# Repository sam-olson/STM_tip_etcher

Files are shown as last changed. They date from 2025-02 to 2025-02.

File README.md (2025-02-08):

# STM Tip Etcher

## Preliminary
This repository contains design files for building a microcontroller-based etcher for creating scanning tunneling microscopy (STM) tips from tungsten wire. The system works by applying a voltage between two tungsten electrodes immersed in an etchant (in this case, 1 M NaOH). The resistance between the two electrodes is monitored through a voltage divider formed between the electrodes and a 100 Ω reference resistor. The output voltage of the divider is read by an analog input pin on the microcontroller. When a spike in resistance between the etching electrodes is detected, a transistor switch shuts off power to the tip, preventing over-etching and rounding of the tip. Using tips etched via this system, high resolution STM images of highly-oriented pyrolytic graphite (HOPG) have been obtained.

The following items are required to assemble this system:

*Equipment*

- Soldering iron
- 3D-printer

*Parts (see the included Bill of Materials for sourcing)*

- Arduino Nano (x1)
- 300 Ω resistor (x1)
- 100 Ω resistor (x2)
- Green LED (x1)
- 2N3904 NPN transistor (x1)
- M4x6.4mm heat set insert (x2)
- M4x8mm set screw (x2)
- 5x7 cm perfboard (x1)
- M3x14mm socket head screw (x4)
- M3x11mm spacer (x4)
- M3x3.8mm heat set insert (x4)

## Build Instructions
### Assembling the Circuit

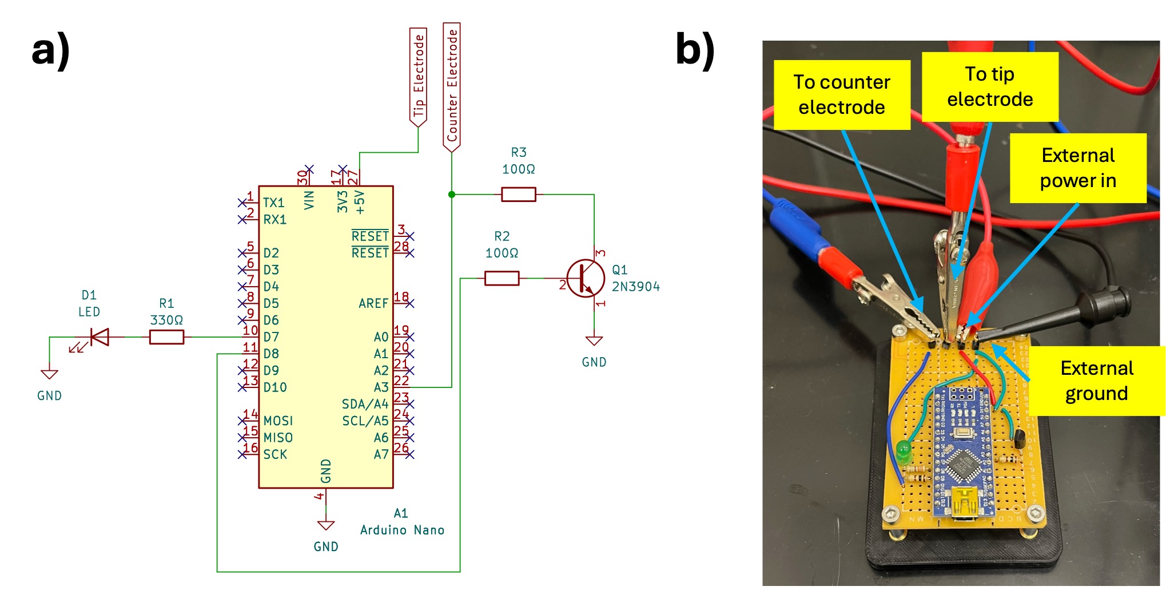
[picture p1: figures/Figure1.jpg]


Figure 1: a) Electrical schematic for the tip etching set up, b) assembled circuit board with header pins labeled

1. Solder electrical components onto a 5x7 cm perfboard following the schematic shown in Fig. 1
2. Power can be supplied to the electrodes from the Arduino’s 5V pin, or an external benchtop power supply
can be used if the current required is ≥ 500 mA or a different voltage is required. If an external power supply is used, it can also power the Arduino through the VIN pin (as long as the voltage is ≤ 12 V)
3. Header pins and alligator clip cables can be used for interfacing with the tungsten tip and counter electrodes

### 3D-Printing Components
3D-print the STEP files for the electrode holding fixture and the circuit board base in PLA (see Fig. 2).

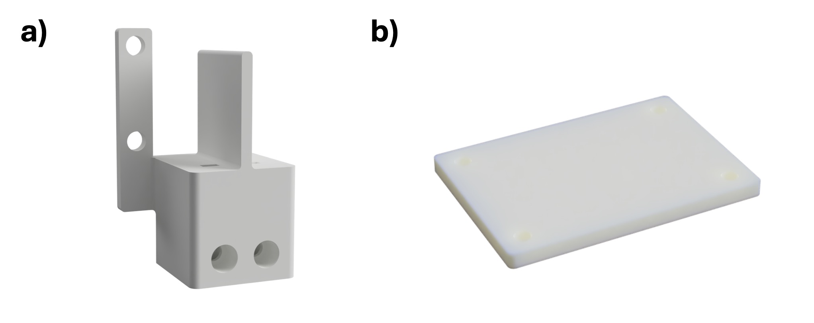
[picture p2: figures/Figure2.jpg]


Figure 2: Renders of 3D-printed components: a) electrode holding fixture (ElectrodeHoldingFixture.step), b) circuit board base (CircuitBoardBase.step)

### Preparing the Electrode Holding Fixture for Use

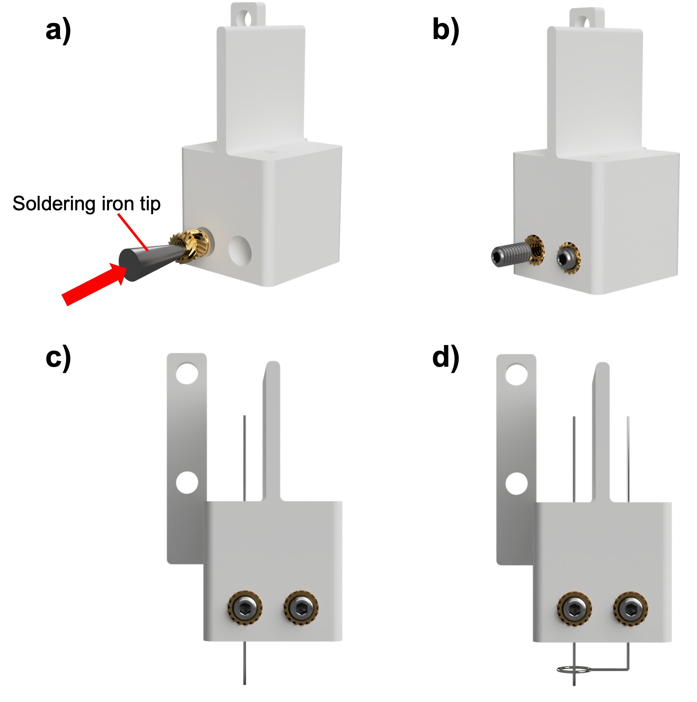
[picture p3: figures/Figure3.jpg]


Figure 3: a) Installing the M4x6.4mm threaded inserts into the electrode holding fixture using a soldering iron tip, b) installation of set screws, c) tip electrode added to electrode holding fixture, d) counter electrode added to electrode holding fixture

1. Using a soldering iron set to 250 °C, heat set two M4x6.4mm threaded inserts into the 6.2 mm holes on the front of the fixture (Fig. 3a)
2. Insert a M4x8mm set screw into each threaded insert, these will be used to press against the tungsten wires to hold them in place during etching (Fig. 3b)
3. Cut a 100 mm length of 0.25 mm diameter tungsten wire and form a 6 mm diameter loop at one end, this will serve as the counter electrode
4. Cut a 75 mm straight length of 0.25 mm diameter tungsten wire, this will serve as the tip electrode
5. Push the tip electrode through the rectangular hole on the left side of the bottom of the electrode holding fixture, leaving roughly 10 mm exposed at the bottom, and fasten it in place by tightening the set screw (Fig. 3c)
6. Push the straight end of the counter electrode through the rectangular hole on the right side of the bottom of the electrode holding fixture
7. Place a straight piece of 0.25 mm tungsten wire into the hole on the lefthand side of the top of the fixture and push it through until 14 mm of wire is exposed between the bottom of the fixture and the top of the loop
8. Create a 90° bend 7 mm from the top of the loop in the counter electrode and situate the loop so that the tip electrode sits in the middle (Fig. 3d)
9. The electrode holding fixture includes two M4-size holes for optional attachment to a stand, however the fixture can also easily be held in place via a lab stand clamp

### Attaching the Circuit Board to the Circuit Board Base

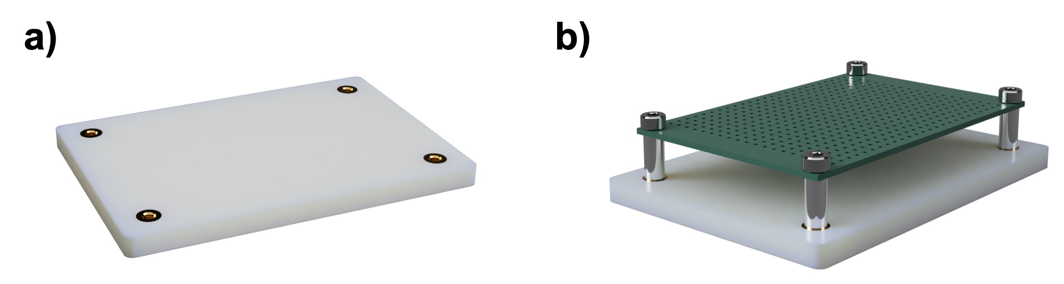
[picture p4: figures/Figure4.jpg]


Figure 4: a) Circuit board base with heat set inserts installed, b) circuit board base with circuit board and standoffs attached

1. Install four M3x3.8mm heat set inserts using a soldering iron set to 250 °C into the 5.5 mm diameter circular recesses on the top of the circuit board stand (Fig. 4a)
2. Place the M3x10mm unthreaded standoffs on the threaded inserts
3. Place the circuit board on top of the unthreaded standoffs and secure it in place with four M3x14mm socket screws (Fig. 4b)
4. Load the firmware (`STM_tip_etcher.ino`) onto the Arduino Nano via the Arduino IDE

## Using the Tip Etcher

### Running an Etch Recipe

1. Prepare an etchant solution of 1 M NaOH in a small dish
2. Attach the electrode holding fixture to a stand with two M4 screws, or place it into a lab stand clamp and lower it until both the tip electrode and the loop of the counter electrode are submerged just below the surface of the etchant
3. Using alligator clips, connect the tip electrode to the 5V pin of the Arduino (or an external power supply), and connect the counter electrode to the counter electrode header (the junction with the 100 Ω resistor and pin A3 on the Arduino)
4. If using an external power supply, ensure that the voltage is kept below 12V and that the ground is tied to the ground pin of the Arduino
5. Turn on the power supply/Arduino, this will begin the tip etching process
6. For a voltage of 5V, a counter electrode loop of 6 mm, and a 1 M NaOH etchant, the etch time is typically around 20 minutes
7. Once the bottom of the tip electrode drops off into the etchant, the resistance between the tip and counter electrode will increase drastically and the microcontroller will automatically stop the power to the electrodes to prevent overetching. The LED will illuminate at this point to indicate that the etching is complete

### Modifying the Firmware
The firmware for the system (`STM_tip_etcher.ino`) is designed to be easy to modify if necessary. There are two important variables for etch profile modification: the voltage threshold below which the etching halts (variable `v_threshold`), and the minimum etching time before cut off can occur (variable `t_threshold`). Variation in one of several experimental parameters can result in the need to modify the voltage and time thresholds. For example, a larger counter electrode diameter may result in a higher final resistance (and so a lower voltage threshold), while an increase in etchant molarity can result in a lower final resistance (and so higher voltage threshold) and/or a shorter etch time. The firmware prints the voltage reading to the serial port during etching, so it is advised to monitor this during several etches once the physical arrangement of your set up is finalized to determine where to set your thresholds.

## Results
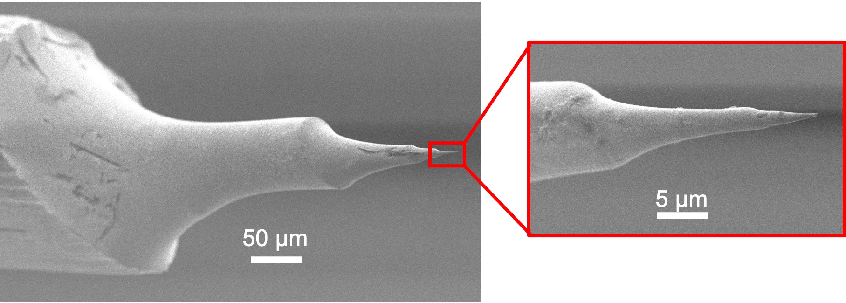
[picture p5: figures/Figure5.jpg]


Figure 5: An STM tip etched from 0.25 mm tungsten wire using this system

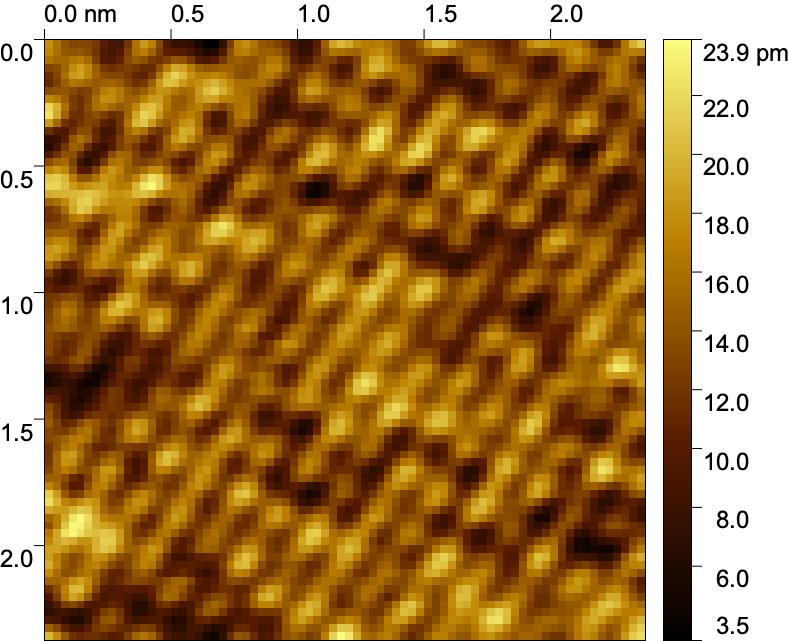
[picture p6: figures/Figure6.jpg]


Figure 6: STM micrograph of highly oriented pyrolytic graphite (HOPG) taken using a tip etched with this system

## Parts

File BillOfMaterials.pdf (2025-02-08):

ITEM | SUPPLIER | PART NUMBER | QUANTITY | | UNIT COST | EXTENDED
COST
ARDUINO NANO | Arduino | A000005 | 1 | $ 24.90 $ | 24.90
330 Ω RESISTOR | Digi-Key | CF14JT330RCT-ND | 1 | $ | 0.10 $ | 0.10
100 Ω RESISTOR | Digi-Key | CF14JT100RCT-ND | 2 | $ | 0.10 $ | 0.20
GREEN LED | Digi-Key | 754-1273-ND | 1 | $ | 0.27 $ | 0.27
2N3904 NPN TRANSISTOR | Digi-Key | 2N3904FS-ND | 1 | $ | 0.28 $ | 0.28
PERFBOARD 76.2X50.8 MM | Digi-Key | 3132-ST-PERF-2-3-ND | 1 | $ | 3.49 $ | 3.49
M3X14MM SOCKET HEAD SCREWS | McMaster-Carr | 91292A027 | 4 | $ | 0.08 $ | 0.31
M3X10MM SPACERS | McMaster-Carr | 94669A105 | 4 | $ | 0.56 $ | 2.24
M3X3.8MM HEAT SET INSERTS | McMaster-Carr | 94180A331 | 4 | $ | 0.20 $ | 0.80
M4X6.4MM HEAT SET INSERTS | McMaster-Carr | 94459A160 | 2 | $ | 0.22 $ | 0.44
M4X8MM SET SCREWS | McMaster-Carr | 92605A113 | 2 | $ | 0.18 $ | 0.35
Total: | $ | 33.38

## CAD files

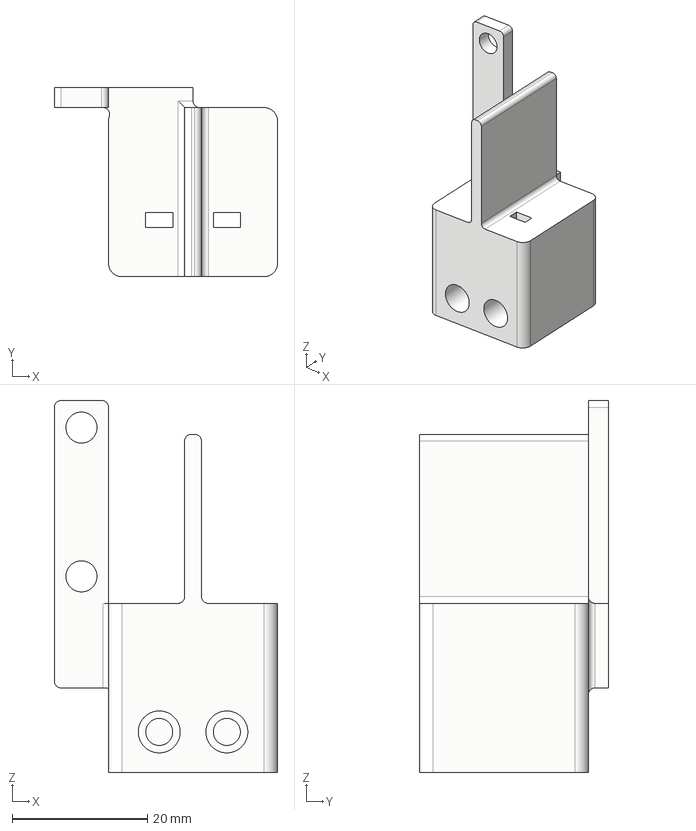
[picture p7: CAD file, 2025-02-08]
3d_printing/ElectrodeHoldingFixture.step
33.0 x 28.0 x 55.0 mm

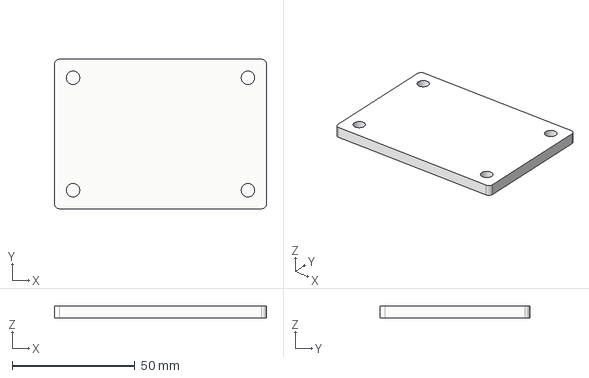
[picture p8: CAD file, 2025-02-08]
3d_printing/CircuitBoardBase.step
86.2 x 60.8 x 5.00 mm

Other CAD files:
3d_printing/CircuitBoardBase.f3d
3d_printing/ElectrodeHoldingFixture.f3d

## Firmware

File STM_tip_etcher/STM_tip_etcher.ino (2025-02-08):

int readPin = 3;          // pin reading Vout of voltage divider formed with electrodes
int basePin = 8;          // pin that activates transistor switch that controls delivery of power to electrodes 
int ledPin = 7;           // pin that activates LED indicator

// threshold variables
float v_threshold = 0.2;  // voltage threshold, below which power to electrodes is shut off
float t_threshold = 0.5;  // time threshold in minutes below hich power to electrodes will not be shut off even if voltage threshold is reached

// variables for storing data
float voltage;
int N = 0;
float sum_v = 0.0;
float average = 0.0;

/* Cuts voltage to electrodes until Arduino is restarted */
void cut_voltage()
{
  digitalWrite(basePin, LOW);
  digitalWrite(ledPin, HIGH);
  Serial.println("Etching stopped");
  while (1)
  {
    continue;
  }
}

/* Converts milliseconds to minutes */
float milli_to_min(unsigned long t)
{
  return t / 60000.0;
}

void setup() {
  Serial.begin(115200);
  pinMode(basePin, OUTPUT);
  pinMode(ledPin, OUTPUT);
  
  digitalWrite(basePin, HIGH);
  digitalWrite(ledPin, LOW);

}

void loop() {
  voltage = 5.0 * (analogRead(readPin) / 1023.0);

  sum_v += voltage;
  N++;

  // Average every 50 cycles to smooth out transient spikes
  if (N == 50)
  {
    Serial.print(milli_to_min(millis()), 4);
    Serial.print(",");
    Serial.println(average);
    average = sum_v / N;
    
    sum_v = 0;
    N = 0;
  }

  // if you are past the time threshold...
  if (milli_to_min(millis()) >= t_threshold)
  {
    // if you are below the voltage threshold...
    if (average <= v_threshold) 
    {
      Serial.print(milli_to_min(millis()), 4);
      Serial.print(",");
      Serial.println(average);

      // cut voltage to the electrodes to stop etching of the tip
      cut_voltage();
    }
  }
  delay(10);
}
